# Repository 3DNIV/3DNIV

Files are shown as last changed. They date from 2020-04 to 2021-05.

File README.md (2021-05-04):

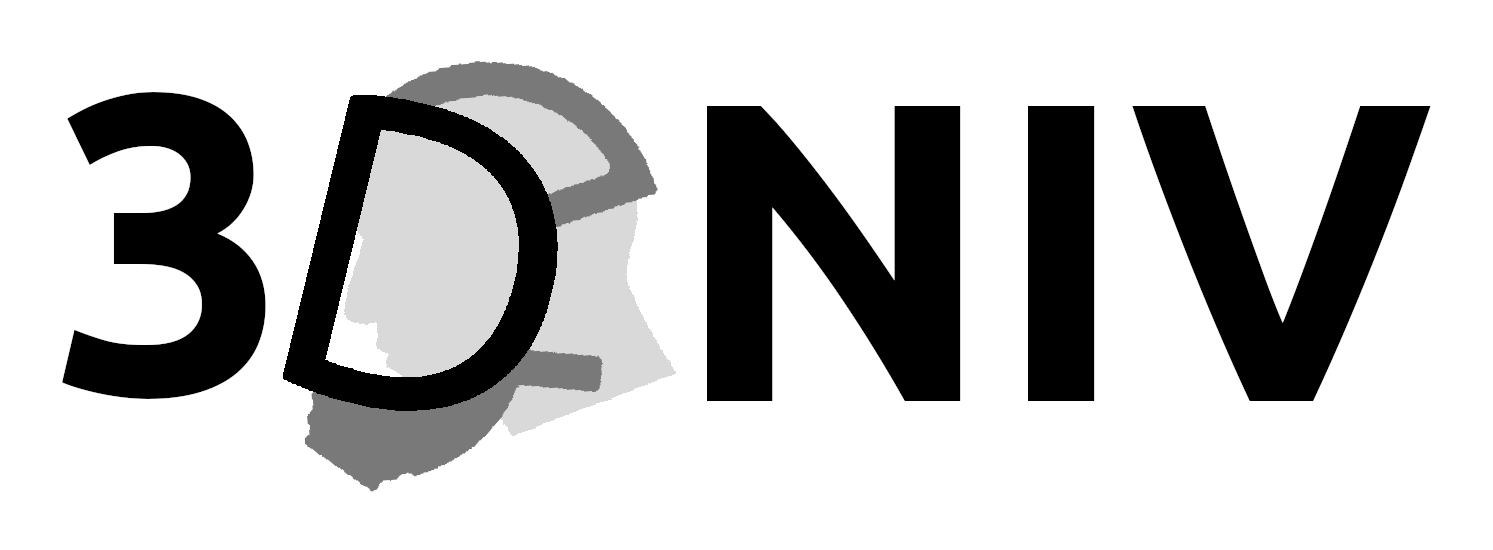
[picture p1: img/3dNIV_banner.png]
3DNIV


## 3DNIV

This is the project repository for the:    
**A Novel Dual Non-Invasive Ventilator Continuous Positive Airway Pressure Non-Aerosolization Circuit for Emergency Use in the COVID-19 Pandemic**

**Cite this work as:**   
_Vaughan, T.J., Kirrane, F., Moerman, K.M., Cahill, T., O’Regan, A. and O’Keeffe, D.T., 2020. A Novel Dual Non-Invasive Ventilator Continuous Positive Airway Pressure Non-Aerosolization Circuit for Emergency Use in the COVID-19 Pandemic. Journal of Open Hardware, 4(1), p.3. DOI: [http://doi.org/10.5334/joh.23](http://doi.org/10.5334/joh.23)_

**Long term archived version:** 

## Licenses
Hardware:     
Documentation and other content: 

## Table of contents
- [Project Summary](#Summary)  
- [Documentation](#Application)  
- [Contributing](#Contributing)  
- [Code of conduct](#CodeOfConduct)  
- [License](#License)  

## Project summary 
The COVID-19 pandemic is a public health emergency of unprecedented scale. The surge in clinical cases of patients with severe respiratory illness has overwhelmed the traditional capacity of healthcare systems worldwide. Continuous Positive Airway Pressure (CPAP) delivered through Non-Invasive Ventilation (NIV) has been shown to be useful in caring for patients with COVID-19. In particular patients with early stage milder acute hypoxemic respiratory failure can benefit from NIV CPAP therapy, though there is an acknowledged risk of COVID-19 aerosolization with traditional circuit use. Furthermore, given the surge in clinical care demand, there is an acute global shortage of ventilators, including NIV devices and therefore innovative methods are needed to increase NIV capacity and ameliorate infectious aerosolization. This project presents an emergency use modified dual NIV CPAP Circuit that uses a 3D printed splitter designed to work with traditional international NIV CPAP tubing standards and a 3D printed respiratory face mask knuckle to allow for distal expiratory breath exhalation through a viral filter rather than through an open to air proximal valve, which is the traditional NIV CPAP configuration. We expect that this work will increase global NIV CPAP capacity and ameliorate aerosolization of COVID-19 in patients undergoing therapy in an emergency scenario. 

### The standard NIC CPAP configuration
<div>
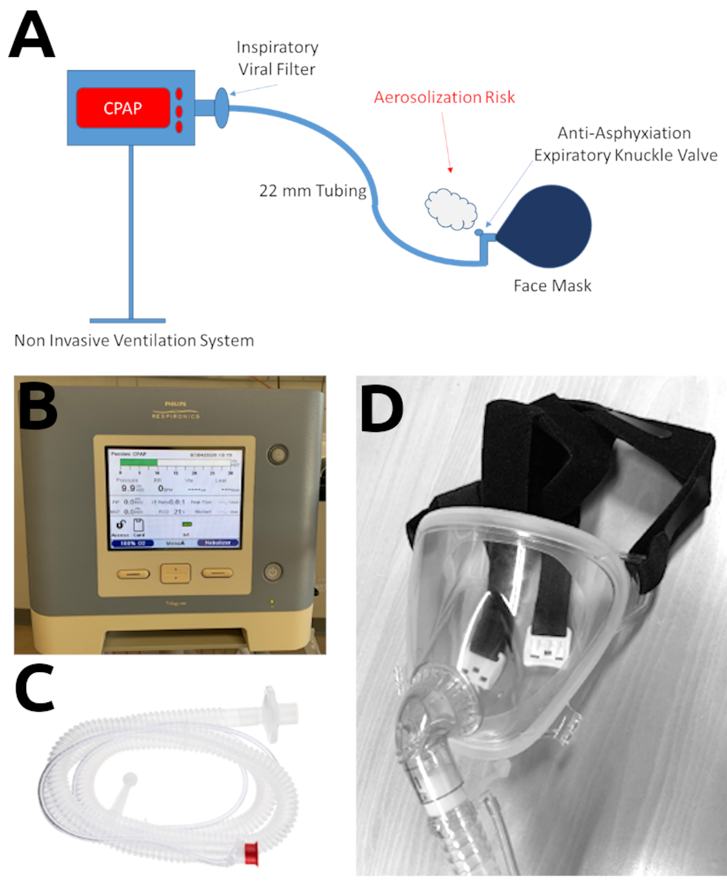
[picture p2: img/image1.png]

</div>
(a) Standard NIV CPAP Configuration b) Standard NIV Machine (c) Standard NIV 22mm Tubing Circuit and (d) Standard (22mm) NIV Facemask with expiratory knuckle valve.   

### The modified Dual NIV CPAP.
<div>
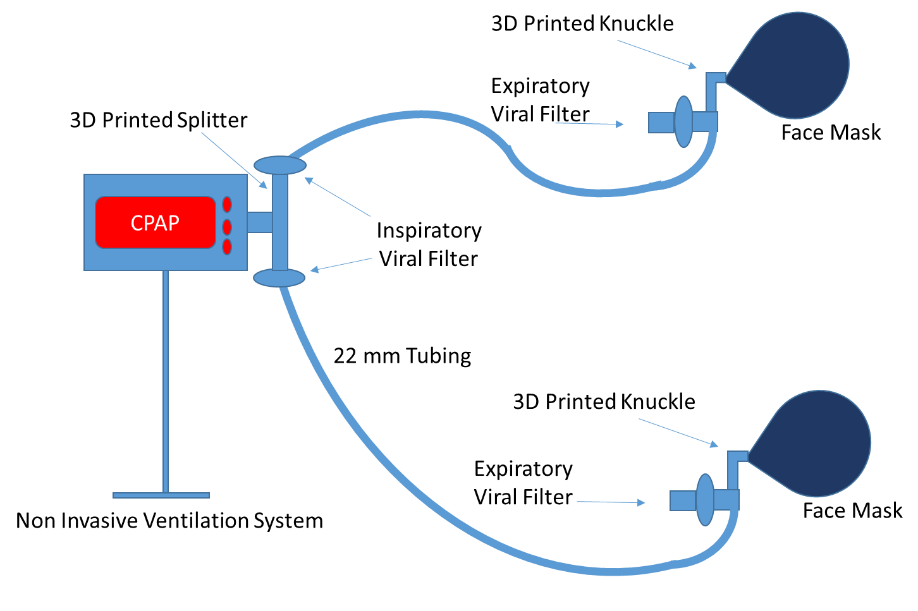
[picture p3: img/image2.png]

</div>
System-level schematic of the modified Dual NIV CPAP.

### 3D printed components
<div>
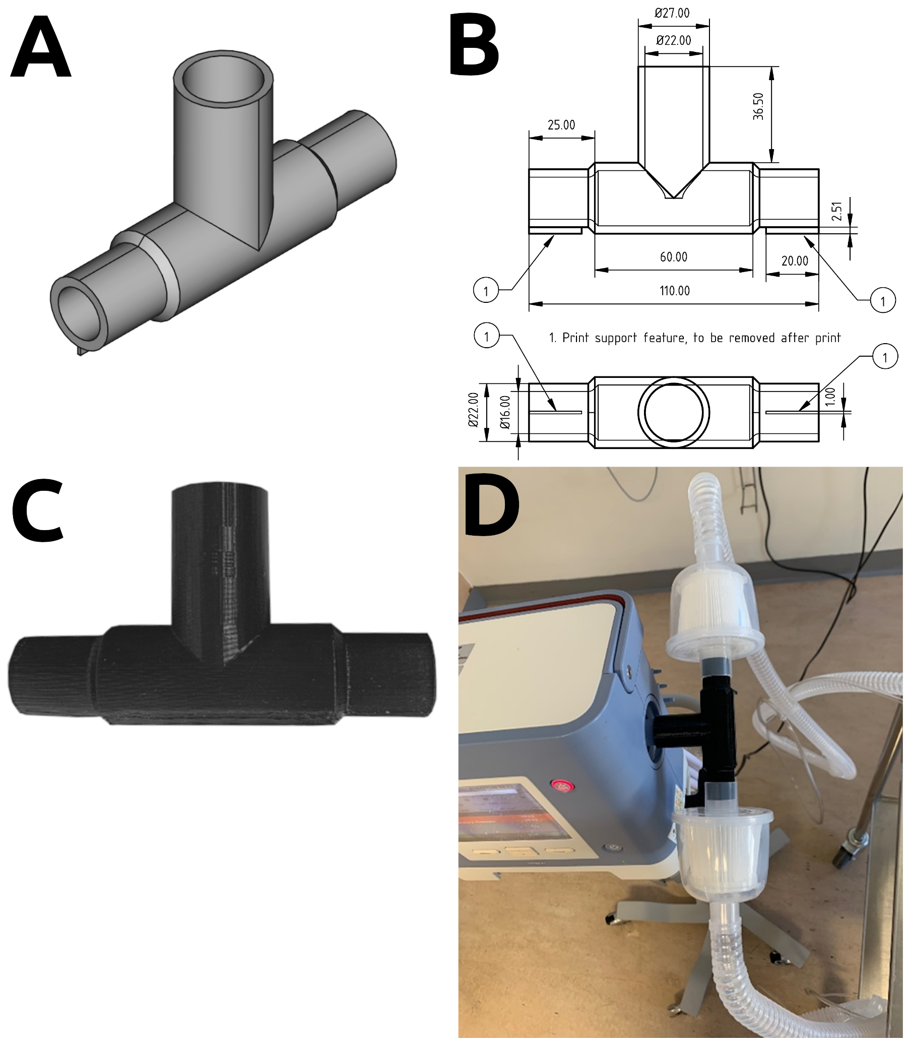
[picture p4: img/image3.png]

</div>
T-Piece component; (a) mechanical drawing with characteristic dimensions; (b) 3D Printed PLA T-Piece and (c) T-Piece connected to NIV machine/tubing.    

<div>
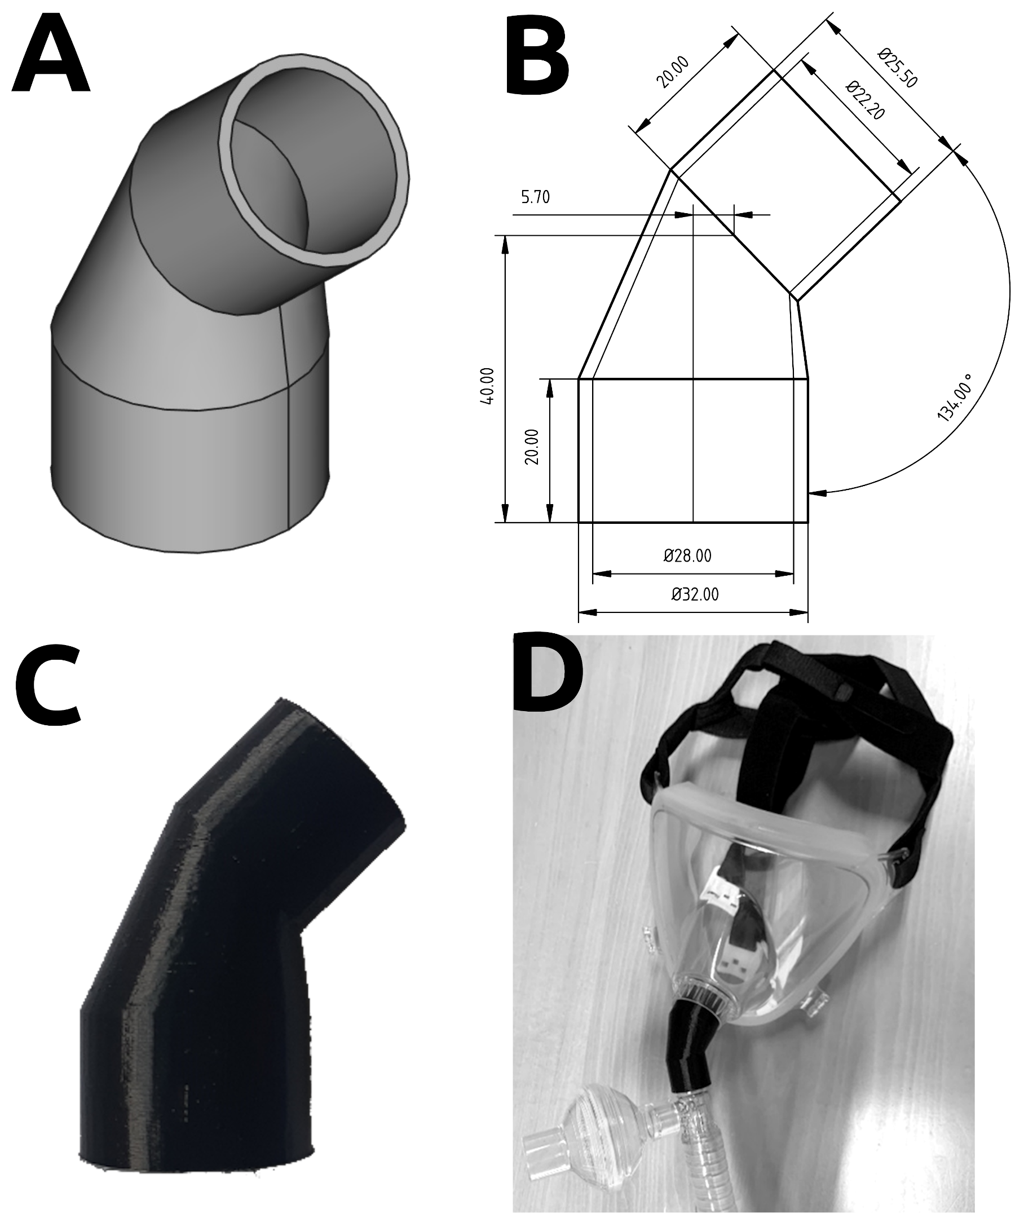
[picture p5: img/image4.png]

</div>
3D Printed Knuckle (a) mechanical drawing with characteristic dimensions; (b) 3D Printed PLA component and (c) T-Piece connected to facemask.  

## Documentation  
The documentation is in the /docs folder and takes the form of a MarkDown file, see: [documentation.md](https://github.com/3DNIV/3DNIV/blob/master/docs/documentation.md).

## Contributing  
We'd love for you to contribute to this project! We welcome all sorts of contributions including design, testing, documentation, and documentation translations. To help simple fork or clone this repository to start working and [post a new issue](https://github.com/Kevin-Mattheus-Moerman/3DNIV/issues/new/choose) if you have any questions. You may propose changes by creating a [pull-request](https://github.com/Kevin-Mattheus-Moerman/3DNIV/pulls).

## Code of conduct  
See: [COC.md](https://github.com/Kevin-Mattheus-Moerman/3DNIV/blob/master/COC.md)

## LICENSE 
The hardware contained and described in this repository is licensed under the [CERN Open Hardware Licence Version 2 - Strongly Reciprocal](https://github.com/Kevin-Mattheus-Moerman/3DNIV/blob/master/LICENSE) (see also: [https://cern-ohl.web.cern.ch/](https://cern-ohl.web.cern.ch/)). All other content (e.g. documentation) is released under the [CC-BY-4.0 license](https://creativecommons.org/licenses/by/4.0/legalcode).

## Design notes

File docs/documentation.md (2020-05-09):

# Documentation

## Table of contents
- [Project repository organisation](#Organisation)  
- [System overview](#System)  
- [Required components](#Components)  
- [Manufacturing instructions](#Manufacture)  
- [Assembly instructions](#Assembly)  
- [Testing instructions](#Testing)  

## Project repository organisation 
| Content         | Project location  | Repository link                                   |
| :-------------  |:-------------     | :-------------                                    |
| CAD files       | /CAD              | https://github.com/3DNIV/3DNIV/tree/master/CAD    |
| gcode           | /gcode            | https://github.com/3DNIV/3DNIV/tree/master/gcode  |
| Documentation   | /docs             | https://github.com/3DNIV/3DNIV/tree/master/docs   |
| Images          | /img              | https://github.com/3DNIV/3DNIV/tree/master/img    |

## System overview 
The figure below shows the system overview. The T-piece splitter is shown connected to the CPAP unit and the inspiratory viral filters. Further more the tubing leading to the face mask is shown. At the face mask the knuckle connects to the mask and an expiratory viral filter.

    
A system-level schematic of the proposed modified Dual NIV CPAP circuit.

## Required Components 
### Ventilator Unit
The modified Dual NIV CPAP circuit depends on a pressure-control ventilator unit, with the circuit here using a Philips Respironics Trilogy 202™ ventilator. The circuit should also be compatible with other similar units. 
### Viral filters
The modified circuit uses viral filters connect through 22mm ports at inspiratory (Servo Duo Guard, Maquet Gettinge) and expiratory  (VIROBAC II, King Systems) ends
### Masks
The circuit uses an NIV facemask (SE Maxshield™, Pulmodyne) connected through a swivel 32mm port. 
### Test Lung
Two 1L test lungs (Test Lung 190, Maquet™, Wayne, New Jersey) are required to test the system setup prior to general use. 
### Tubing
All of the hardware listed here is designed to connect to standard respirator tubing (BiTrac™ Circuit, Pulmodyne) that uses universal 22mm ports/connections.

## Manufacturing instructions 

### The T-piece splitter 

**CAD file**: [/CAD/NIV_CPAP_T_Piece.FCStd](https://github.com/3DNIV/3DNIV/blob/master/CAD/NIV_CPAP_T_Piece.FCStd)  
**Technical drawing**: [/CAD/NIV_CPAP_T_Piece.pdf](https://github.com/3DNIV/3DNIV/blob/master/CAD/NIV_CPAP_T_Piece.pdf)    
**gcode file**: [/gcode/NIV_CPAP_T_Piece_GCODE.GCODE](https://github.com/3DNIV/3DNIV/blob/master/gcode/NIV_CPAP_T_Piece_GCODE.GCODE)    

   
The novel T-piece component. A) The CAD file view, B) part of the technical drawing showing characteristic dimensions, C) the PLA 3D printed T-Piece, D) and the T-Piece connected to a NIV machine and tubing.

This part can be 3D printed from Polylactic Acid (PLA) with an Ultimaker S5 (Ultimaker BV, The Netherlands) using an extrusion-based layer-by-layer process at a resolution of 200 micron and 100 % infill to prevent air leaks.   

Users may use the provided [gcode](https://github.com/3DNIV/3DNIV/blob/master/gcode/NIV_CPAP_T_Piece_GCODE.GCODE) for 3D printing or develop their own.
The orientation of printing used here is upright (such that the T defines an upside down T on the printing platform). 3D printing takes X minutes and about X grams material.    

After 3D printing any 3D printed support structures should be removed.    

The CAD design geometry includes (as shown in the [technical drawing](https://github.com/3DNIV/3DNIV/blob/master/CAD/NIV_CPAP_T_Piece.pdf)) two small features added to provide support during 3D printing. After 3D printing these should be removed. If one does not wish to include these features the [CAD source file](https://github.com/3DNIV/3DNIV/blob/master/CAD/NIV_CPAP_T_Piece.FCStd) can be adjusted (the two last features in the CAD feature tree define these added print supports), and new 3D printing files can be created.

### The knuckle piece

**CAD file**: [/CAD/NIV_CPAP_Knuckle.FCStd](https://github.com/3DNIV/3DNIV/blob/master/CAD/NIV_CPAP_Knuckle.FCStd)  
**Technical drawing**: [/CAD/NIV_CPAP_Knuckle.pdf](https://github.com/3DNIV/3DNIV/blob/master/CAD/NIV_CPAP_Knuckle.pdf)    
**gcode file**: [/gcode/NIV_CPAP_Knuckle_GCODE.GCODE](https://github.com/3DNIV/3DNIV/blob/master/gcode/NIV_CPAP_Knuckle_GCODE.GCODE)    

   
The novel T-piece component. A) THe CAD file view, B) part of the technical drawing showing characteristic dimensions, C) the PLA 3D printed T-Piece, D) and the T-Piece connected to a NIV machine and tubing.

This part can be 3D printed from Polylactic Acid (PLA) with an Ultimaker S5 (Ultimaker BV, The Netherlands) using an extrusion-based layer-by-layer process at a resolution of 200 micron and 100 % infill to prevent air leaks.   

Users may use the provided [gcode](https://github.com/3DNIV/3DNIV/blob/master/gcode/NIV_CPAP_Knuckle_GCODE.GCODE) for 3D printing or develop their own.
The orientation of printing used here is upright (such that the larger cylindrical surface is placed flat on the the printing platform). 3D printing takes X minutes and about X grams material.    

After 3D printing any 3D printed support structures should be removed.    

## Assembly instructions 
Connect the female port of the T-piece splitter directly to the ventilator outflow. Connect separate inspiratory viral filters to the two male ports of the T-piece splitter. Connect standard respirator tubing to these viral filters to form the two limbs of the dual circuit. At the end of both tubing limbs, connect an expiratory viral filter and the 3D printed knuckle feature. Connect each knuckle component to NIV face masks through the swivel port.

## Testing instructions 
The Dual NIV CPAP Circuit should be tested prior to use. Follow the assembly instructions above, but connect the system to two 1L test lungs (Test Lung 190, Maquet™, Wayne, New Jersey) instead of the NIV face mask (SE Maxshield™, Pulmodyne). Run the ventilator in pressure-control CPAP configuration to establish that it is capable of delivering 10 cm H₂0 by inflating both test lungs for at least 60 seconds.

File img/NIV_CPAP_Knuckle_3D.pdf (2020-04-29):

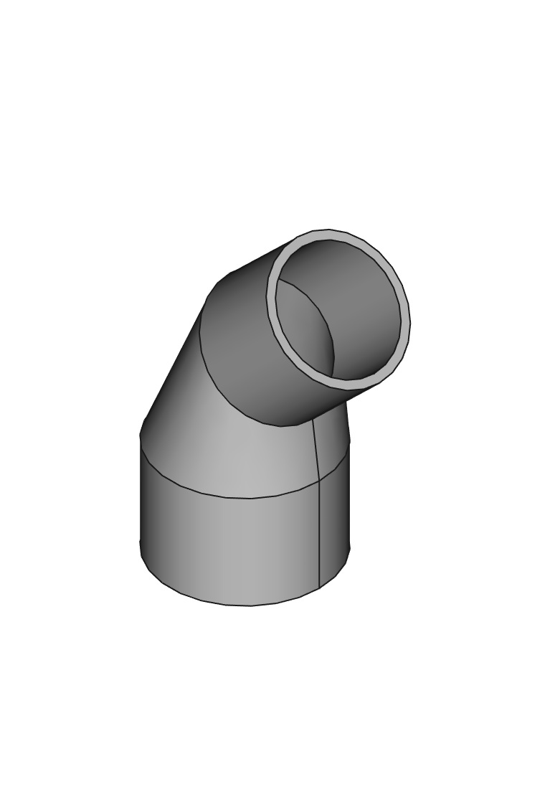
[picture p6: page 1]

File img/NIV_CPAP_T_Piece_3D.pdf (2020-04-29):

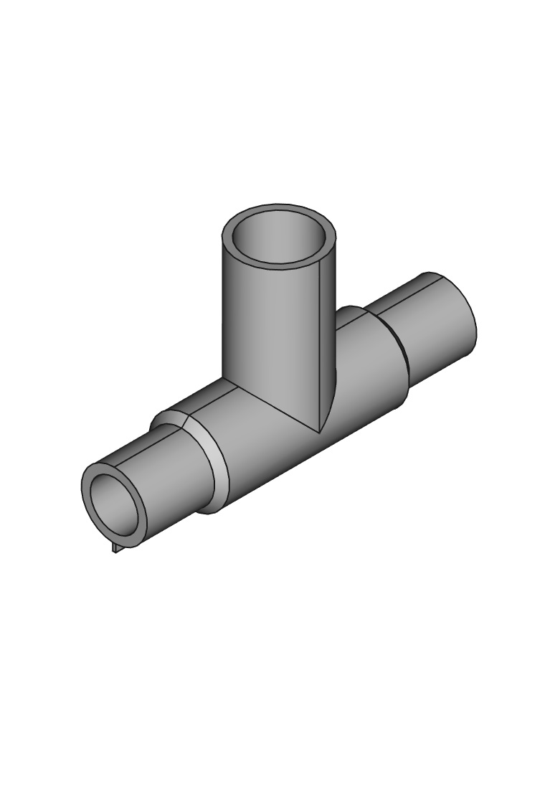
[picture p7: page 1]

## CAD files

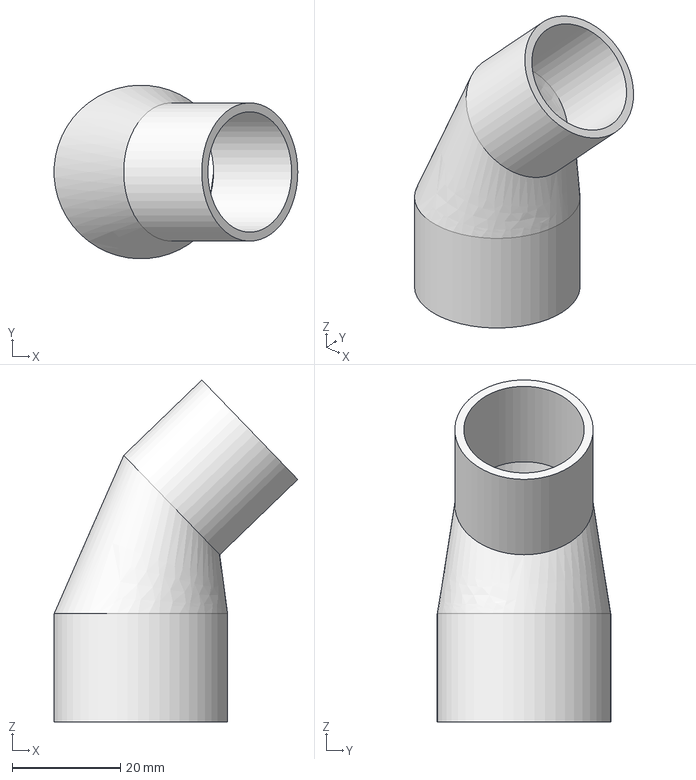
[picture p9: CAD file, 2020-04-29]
CAD/NIV_CPAP_Knuckle.FCStd
44.9 x 32.0 x 63.0 mm

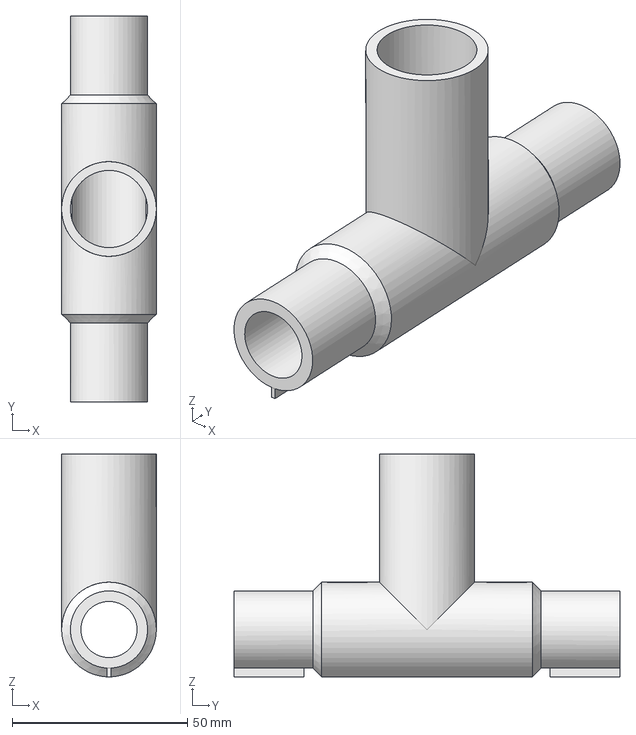
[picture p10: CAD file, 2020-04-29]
CAD/NIV_CPAP_T_Piece.FCStd
27.0 x 110.0 x 63.5 mm

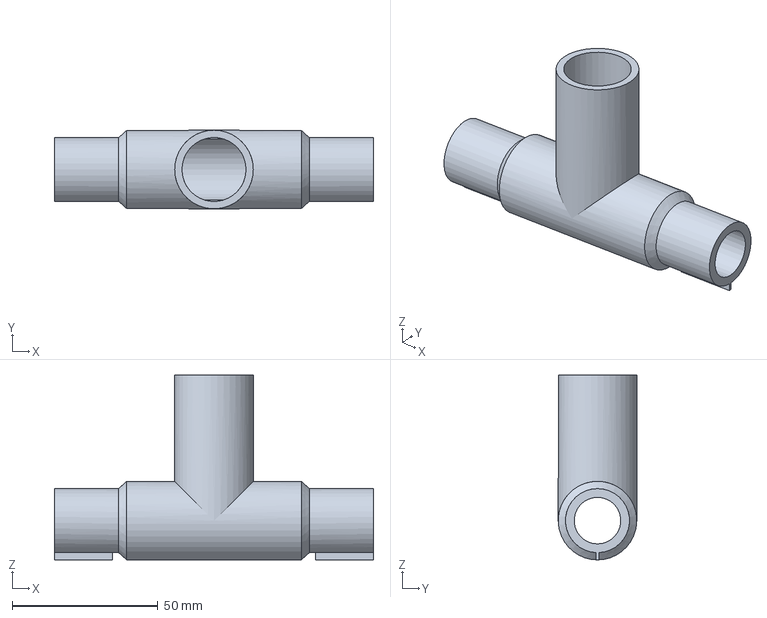
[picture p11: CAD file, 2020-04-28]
CAD/NIV_CPAP_T_Piece_3MF.3mf.3mf
109.6 x 27.0 x 63.5 mm

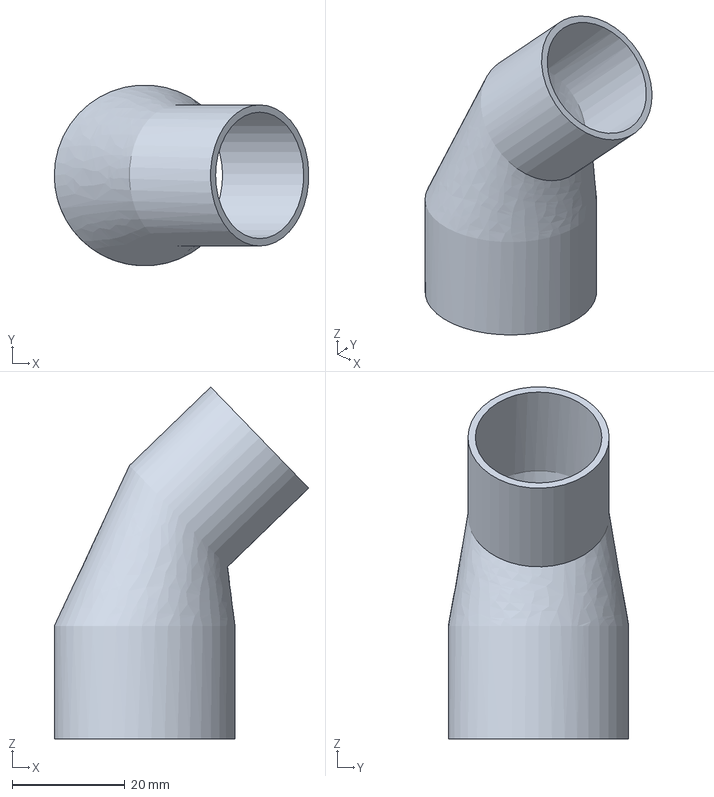
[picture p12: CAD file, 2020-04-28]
CAD/NIV_CPAP_Knuckle.3mf.3mf
45.1 x 32.0 x 62.3 mm

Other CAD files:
CAD/NIV_CPAP_T_Piece_IGES.IGES
CAD/NIV_CPAP_Knuckle_IGES.IGES
CAD/NIV_CPAP_Knuckle.stl
CAD/NIV_CPAP_T_Piece.stl

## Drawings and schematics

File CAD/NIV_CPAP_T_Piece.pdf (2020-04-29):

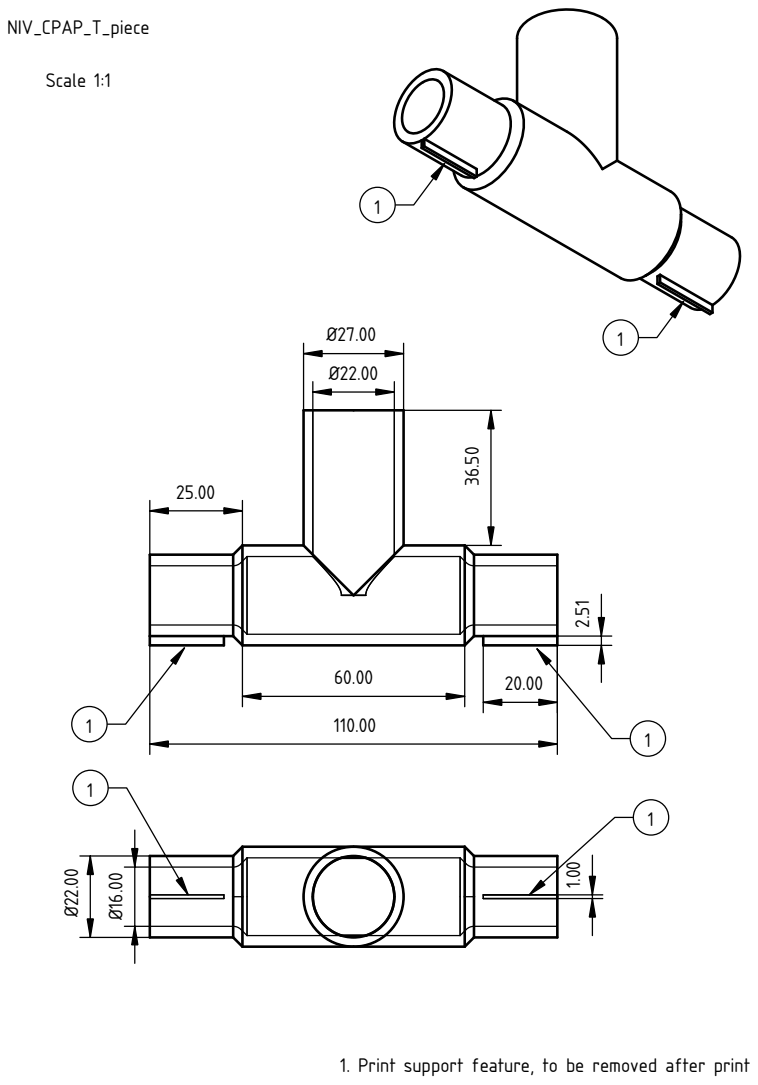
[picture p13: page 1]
Scale 1:1; NIV_CPAP_T_piece

1. Print support feature, to be removed after print

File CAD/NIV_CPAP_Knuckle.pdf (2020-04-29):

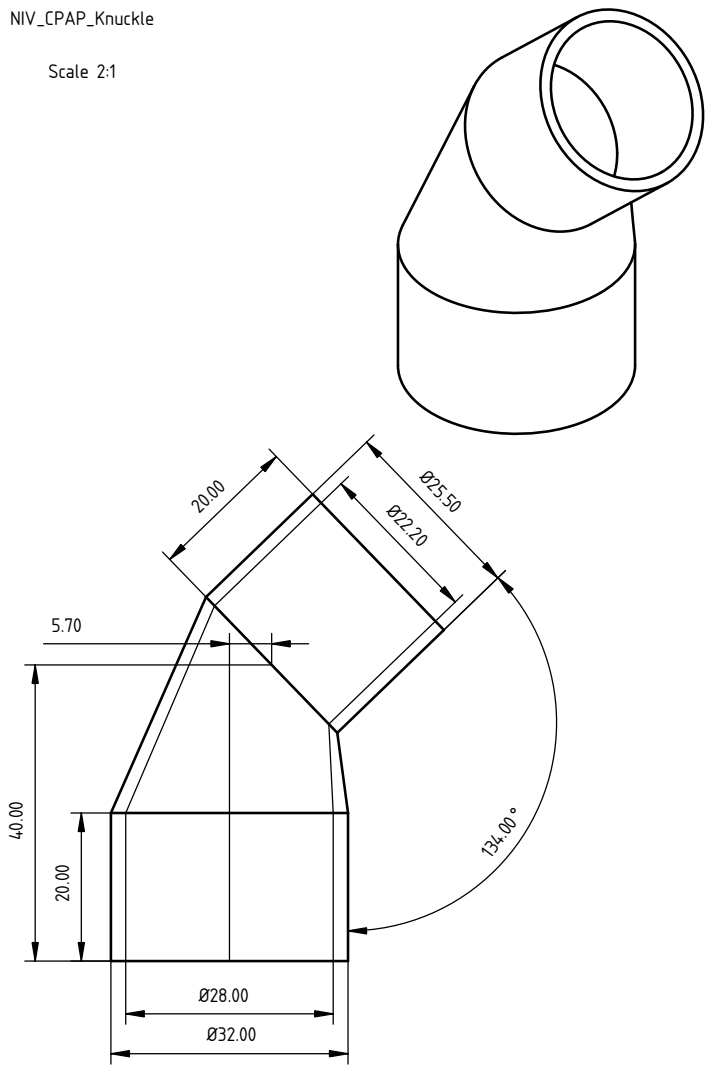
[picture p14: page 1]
Scale 2:1; NIV_CPAP_Knuckle

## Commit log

2020-04-27 Updated readme with images of devices
2020-04-28 Added gcode and cad content
    [NIV_CPAP_Knuckle.3mf.3mf, NIV_CPAP_Knuckle_IGES.IGES, NIV_CPAP_T_Piece_3MF.3mf.3mf, NIV_CPAP_T_Piece_IGES.IGES]
2020-04-29 Updated CAD files and renderings
    [NIV_CPAP_Knuckle.FCStd, NIV_CPAP_Knuckle.stl, NIV_CPAP_T_Piece.FCStd, NIV_CPAP_T_Piece.stl]

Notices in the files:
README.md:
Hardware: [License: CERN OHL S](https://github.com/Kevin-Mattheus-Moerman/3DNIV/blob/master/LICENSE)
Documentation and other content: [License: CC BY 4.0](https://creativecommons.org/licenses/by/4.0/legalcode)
